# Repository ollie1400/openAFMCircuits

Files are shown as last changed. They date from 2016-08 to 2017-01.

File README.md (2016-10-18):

# openAFMCircuits

This is the repo for the circuit schematics and layouts for the openAFM board.  Each board is developed on a separate branch.  Current convention is that when the boards are complete and have been manufactured, they are merged with the main branch.  i.e. the main branch should always reflect the current state of the physical boards.

Each board is in a separate subfolder.  Some folders contain text files with "simulation" or "falstadsimulation" or something similar in the name.  These are schematics for a simulation (typically of some part of the circuit).  They can be viewed by going to http://www.falstad.com/circuit/circuitjs.html and importing the text via `File -> Import From Text`.

There are 4 boards that control the openAFM hardware.  These are

1. Main Board
2. Piezo Board
3. Voice Coil Board
4. Input Board

A brief descripion of each board is given below.  For more details look in the folder for each board.  Each board has a pair of 10-pin headers on either side.  These have a female connector on the top, and long lines that extend through the board and produte from the bottom.  These interboard headers allow the boards to stack on top of eachother, whilst sharing 20 common pins.

## Main Board

This board takes in 12V DC from the power supply.  It is responsible for regulating this down to 5V, and distributing power (12V, 5V and GND) to the other boards via the interboard headers.  It is responsible for generating a constant current for the laser diode in the DVD head, and routing signals from other boards (via the interboard headers) to the DVD head.  The DVD head connects directly to this board via a ribbon cable.  The board takes signals from the arduino (via the 10-pin female header) and routes them to the appropriate pins on the interboard headers to be shared with the other boards.

## Input Board

This board deals with the inputs from the 4 photodiode quadrants on the DVD head (labelled as A, B, C and D).  It routes these directly to an ADC, calculates differences and summs in hardware and routes these to another ADC.

## Piezo Board

This board has a 4 channel DAC which is used to control the signals to move each of the 4 piezo quadrants that control the stage movement.  It takes the 4 voltages from the DAC and amplifies them to give a larger range.

## Voice Coil Board

Has a DAC that, along with a pair of push-pull amplifiers, generates the required current to drive the voice coils in the DVD head (focus and tracking).

# I2C Addresses

Here are the I2C addresses of all ICs connected to the I2C bus.

**Part**  | AD5252BRUZ100 | AD5252BRUZ100 | AD5593RBRUZ | AD5696RARUZ | AD5696RARUZ
----------|---------------|---------------|-------------|-------------|------------
**Address (bin)** | 0101111 | 0101100 | 0010001 | 0001100 | 0001111
**Address (hex)** | 2F | 2C | 11 | C | F
**Address (dec)** | 47 | 44 | 17 | 12 | 15
**How?** | AD0 & AD1 to 5V | AD0 & AD1 grounded | A0 to 5V | A0 & A1 grounded | A0 & A1 to 5V
**Description** | Gain Dual digital pot | Gain Dual digital pot | Input ADC | Piezo DAC | Voice Coil DAC
**Board** | Input | Input | Input | Piezo | Voice Coil
**Board Label** | U2 | U6 | U3 | ? | ?

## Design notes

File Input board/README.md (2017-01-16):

# Input Board

This board deals with the photodiode signals from the DVD head.

# I2C Addresses

Here are the I2C addresses of the ICs on this board

**Part**  | AD5252BRUZ100 | AD5252BRUZ100 | AD5593RBRUZ
----------|---------------|---------------|-------------
**Address (bin)** | 0101111 | 0101100 | 0010001
**Address (hex)** | 2F | 2C | 11 
**Address (dec)** | 47 | 44 | 17
**How?** | AD0 & AD1 to 5V | AD0 & AD1 grounded | A0 to 5V
**Description** | Gain Dual digital pot | Gain Dual digital pot | ADC
**Board Label** | U2 | U6 | U3

# Layout Image

For ease of access here is the layout of the board (from the top)

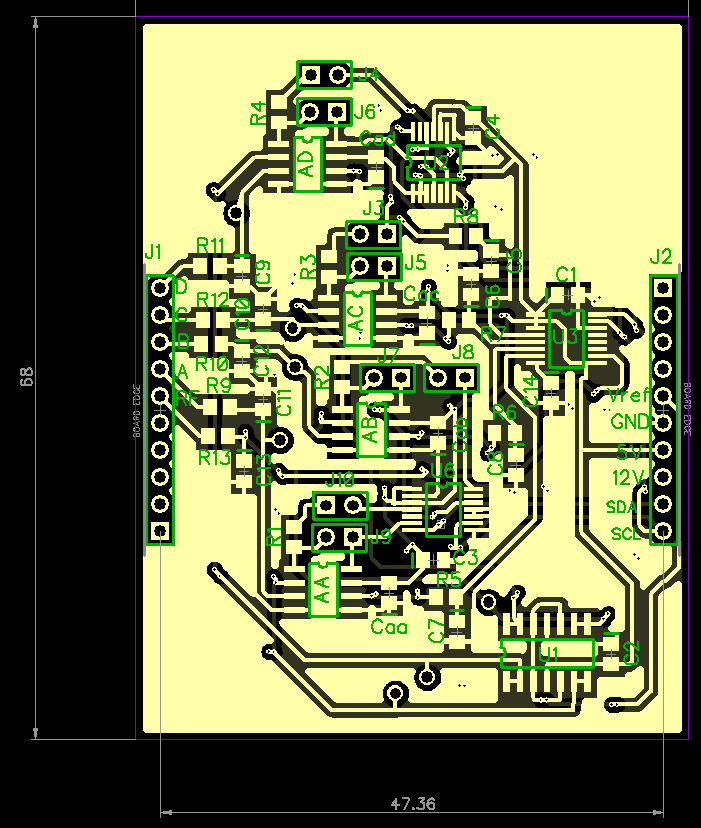
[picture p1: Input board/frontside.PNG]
Layout of front side of input board


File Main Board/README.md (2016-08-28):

# openAFMCircuits

This is the repo for the circuit schematics and layouts for the openAFM board.

There are 4 boards that control the openAFM hardware.  These are

1. Main Board
2. Piezo Board
3. Voice Coil Board
4. Input Board

In this repository, each board is on a different branch.

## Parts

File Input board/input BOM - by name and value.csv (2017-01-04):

RefDes | Value | Name | Pattern | Manufacturer | Quantity
AA, AB, AC, AD |  | AD623ARZ-R7 | SOIC-8/150mil | Analog Devices | 4
C1, C14 | 0.1u | CAP_0805 | CAP_0805 |  | 2
C2, C3, C4, C5, C6, C7, C8, C9, C10, C11, C12, C13, Caa, Cab, Cac, Cad | 3.2u | CAP_0805 | CAP_0805 |  | 16
J1, J2 |  | 1-644456-0 | HDR-1x10T/2.54/25x2 | TE Connectivity | 2
J3, J4, J5, J6, J7, J8, J9, J10 |  | 90131-0121 | HDR-2x1T/2.54x2.54/3x5 | Molex | 8
R1, R2, R3, R4 | 1k | RES_0805 | RES_0805 |  | 4
R5, R6, R7, R8, R9, R10, R11, R12, R13 | 5k | RES_0805 | RES_0805 |  | 9
U1 |  | LM324AD | SOIC-14/150mil | Motorola | 1
U2, U6 |  | AD5252BRUZ100 | TSSOP-14 | Analog Devices | 2
U3 |  | AD5593RBRUZ | TSSOP-16 | Analog Devices | 1
 |  |  |  |  | 49

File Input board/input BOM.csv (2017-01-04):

RefDes | Value | Name | Pattern | Manufacturer
AA |  | AD623ARZ-R7 | SOIC-8/150mil | Analog Devices
AB |  | AD623ARZ-R7 | SOIC-8/150mil | Analog Devices
AC |  | AD623ARZ-R7 | SOIC-8/150mil | Analog Devices
AD |  | AD623ARZ-R7 | SOIC-8/150mil | Analog Devices
C1 | 0.1u | CAP_0805 | CAP_0805
C2 | 3.2u | CAP_0805 | CAP_0805
C3 | 3.2u | CAP_0805 | CAP_0805
C4 | 3.2u | CAP_0805 | CAP_0805
C5 | 3.2u | CAP_0805 | CAP_0805
C6 | 3.2u | CAP_0805 | CAP_0805
C7 | 3.2u | CAP_0805 | CAP_0805
C8 | 3.2u | CAP_0805 | CAP_0805
C9 | 3.2u | CAP_0805 | CAP_0805
C10 | 3.2u | CAP_0805 | CAP_0805
C11 | 3.2u | CAP_0805 | CAP_0805
C12 | 3.2u | CAP_0805 | CAP_0805
C13 | 3.2u | CAP_0805 | CAP_0805
C14 | 0.1u | CAP_0805 | CAP_0805
Caa | 3.2u | CAP_0805 | CAP_0805
Cab | 3.2u | CAP_0805 | CAP_0805
Cac | 3.2u | CAP_0805 | CAP_0805
Cad | 3.2u | CAP_0805 | CAP_0805
J1 |  | 1-644456-0 | HDR-1x10T/2.54/25x2 | TE Connectivity
J2 |  | 1-644456-0 | HDR-1x10T/2.54/25x2 | TE Connectivity
J3 |  | 90131-0121 | HDR-2x1T/2.54x2.54/3x5 | Molex
J4 |  | 90131-0121 | HDR-2x1T/2.54x2.54/3x5 | Molex
J5 |  | 90131-0121 | HDR-2x1T/2.54x2.54/3x5 | Molex
J6 |  | 90131-0121 | HDR-2x1T/2.54x2.54/3x5 | Molex
J7 |  | 90131-0121 | HDR-2x1T/2.54x2.54/3x5 | Molex
J8 |  | 90131-0121 | HDR-2x1T/2.54x2.54/3x5 | Molex
J9 |  | 90131-0121 | HDR-2x1T/2.54x2.54/3x5 | Molex
J10 |  | 90131-0121 | HDR-2x1T/2.54x2.54/3x5 | Molex
R1 | 1k | RES_0805 | RES_0805
R2 | 1k | RES_0805 | RES_0805
R3 | 1k | RES_0805 | RES_0805
R4 | 1k | RES_0805 | RES_0805
R5 | 5k | RES_0805 | RES_0805
R6 | 5k | RES_0805 | RES_0805
R7 | 5k | RES_0805 | RES_0805
R8 | 5k | RES_0805 | RES_0805
R9 | 5k | RES_0805 | RES_0805
R10 | 5k | RES_0805 | RES_0805
R11 | 5k | RES_0805 | RES_0805
R12 | 5k | RES_0805 | RES_0805
R13 | 5k | RES_0805 | RES_0805
U1 |  | LM324AD | SOIC-14/150mil | Motorola
U2 |  | AD5252BRUZ100 | TSSOP-14 | Analog Devices
U3 |  | AD5593RBRUZ | TSSOP-16 | Analog Devices
U6 |  | AD5252BRUZ100 | TSSOP-14 | Analog Devices

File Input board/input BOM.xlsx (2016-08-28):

Description | Example URL | Quantity | Place Labels | Comments
3.2uF surface mount capacitors 0805 | http://china.rs-online.com/web/p/ceramic-multilayer-capacitors/7236054/ | 15 | C1, C2, ADC1Cap, ADC2Cap, Cref, Csr, C3, C4, C5, C6, C7, C8, ADCap1, ADCap2, OpCap | Can be anything from 3 to 3.4 uF
10k surface mount resistors 0805 | http://china.rs-online.com/web/p/surface-mount-fixed-resistors/2230562/ | 3 | Rr1, R2, Rr2 | Can be anything from 9.8k to 10.2k
5k surface mount resistors 0805 | http://china.rs-online.com/web/p/surface-mount-fixed-resistors/6791569/ | 12 | R1,R3, R4, R5, R7, R6, R8, R9,R10,R11, R12, R13 | Can be anything from 4.8k to 5.2k
ADS1015IDGSR | http://china.rs-online.com/web/p/general-purpose-adcs/7094550/ | 2 | ADS1015-1, ADS1015-2
AD623ARZ-R7 |  | 2 | AD623-1, AD623-2
30k surface mount resistors 0805 | http://china.rs-online.com/web/p/surface-mount-fixed-resistors/6791263/ | 2 | Rsr1, Rsr2 | Can be anything from 20k to 50k
10 pin female header | http://china.rs-online.com/web/p/pcb-sockets/7655745/ | 2 | J1, J2
2 pin male header | http://china.rs-online.com//web/p/pcb-headers/2518086/ (http://china.rs-online.com/web/p/pcb-headers/2518086/) | 2 | J3, J4
dual opamp, TL072CD | http://china.rs-online.com/web/p/operational-amplifiers/0857907/ | 1 | U1

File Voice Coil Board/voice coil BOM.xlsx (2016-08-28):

Description | Example URL | Label | Quantity
3.2uF surface mount capacitors 0805 | http://china.rs-online.com/web/p/ceramic-multilayer-capacitors/6911161/ | C1, C2, C3, C4, C11 | 4
10k surface mount resistors 0805 | http://china.rs-online.com/web/p/surface-mount-fixed-resistors/2230562/ | R6, R11, R12 | 3
5k surface mount resistors 0805 | http://china.rs-online.com/web/p/surface-mount-fixed-resistors/6791569/ | R1, R2, R3, R4, R7, R8, R9, R10 | 8
LM324D opamps | http://china.rs-online.com/web/p/operational-amplifiers/0858405/ | U9, U10 | 2
FMMT449 (NPN transistors) | http://china.rs-online.com/web/p/bipolar-transistors/6697681/ | U3, U4, U7, U8 | 4
FSB749 (PNP transistors) | http://china.rs-online.com/web/p/bipolar-transistors/8076033/?searchTerm=FSB749 | U1, U2, U5, U6 | 4
DAC (AD5338RBRUZ) | http://china.rs-online.com/web/p/general-purpose-dacs/8209173/?searchTerm=AD5338RBRUZ | DAC1 | 1
1k surface mount resistors 0805 | http://china.rs-online.com/web/p/surface-mount-fixed-resistors/2230427/ | R5 | 1
30k surface mount resistors 0805 | http://china.rs-online.com/web/p/surface-mount-fixed-resistors/6791263/ | R13, R14 | 2
10 pin female header | http://china.rs-online.com/web/p/pcb-sockets/7655745/ | J1, J2 | 2

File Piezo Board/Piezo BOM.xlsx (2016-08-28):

Description | Quantity | URL | Comments | Positions on board
3.2uF surface mount capacitors 0805 | 6 | http://china.rs-online.com/web/p/ceramic-multilayer-capacitors/6911161/ | Can vary from 3-3.5 uF | DaC, Cref, Ca, Cd, Cc, Cb
10k surface mount resistors 0805 | 3 | http://china.rs-online.com/web/p/surface-mount-fixed-resistors/2230562/ | Can vary from 10 to 50kOhm | Rdv1, Rdv2,Rdr
1uF surface mount capacitors 0805 | 1 | http://china.rs-online.com/web/p/ceramic-multilayer-capacitors/4515770/ | Must be 1uF | Cf
5k surface mount resistors 0805 | 8 | http://china.rs-online.com/web/p/surface-mount-fixed-resistors/6791569/ | Can vary from 4.8k to 5.2k | Ra1, Rb1, Rc1, Rd1, Rfa, Rfd, Rfc, Rfb
DAC (AD5696RARUZ) | 1 | http://china.rs-online.com/web/p/general-purpose-dacs/8065471/ |  | DAC1
LTC3260 | 1 | http://china.rs-online.com/web/p/charge-pumps/8516768/ | mounted so that pin 1 is next to the dot | <Unlabelled>
100k surface mount resistors 0805 | 2 | http://china.rs-online.com/web/p/surface-mount-fixed-resistors/2230691/ | Can vary from 90k to 110k | RAGm, RAGp
800k surface mount resistors 0805 | 2 | http://china.rs-online.com/web/p/surface-mount-fixed-resistors/7087004/ | can vary from 780k to 820k | RLAm, RLAp
200k surface mount resistor 0805 | 1 | http://china.rs-online.com/web/p/surface-mount-fixed-resistors/6791064/ | has to be 200k | R14
30k surface mount resistors 0805 | 4 | http://china.rs-online.com/web/p/surface-mount-fixed-resistors/6791263/ | can vary from 28k to 32k | Ra2, Rb2, Rc2, Rd2
10uF surface mount capacitors 0805 | 5 | http://china.rs-online.com/web/p/ceramic-multilayer-capacitors/6911161/ | Should be as close as possible | LmC, LpC, ViC, VoC, OC
10nF surface mount capacitors 0805 | 2 | http://china.rs-online.com/web/p/ceramic-multilayer-capacitors/2644371/ | Should be as close as possible | BmC, BpC
5 pin male header | 1 | http://china.rs-online.com/web/p/pcb-headers/2518121/?searchTerm=W81105T3825RC |  | Piezos
LM324AD | 1 | http://china.rs-online.com/web/p/operational-amplifiers/5171876/ |  | LM324

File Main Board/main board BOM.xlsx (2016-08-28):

Description | Example URL | Quantity | Label on PCB
20 Ohm surface mount resistor 0805 | http://china.rs-online.com/web/p/surface-mount-fixed-resistors/7217615/ | 1 | R7
1k surface mount resistors 0805 | http://china.rs-online.com/web/p/surface-mount-fixed-resistors/2230427/ | 1 | R1
4k7 surface mounts resistor 0805 | http://china.rs-online.com/web/p/surface-mount-fixed-resistors/2230528/ | 2 | R2, R3
10uF capacitor | http://china.rs-online.com/web/p/aluminium-capacitors/0117035/ | 3 | U4, C5, U8
10 pin female header | http://china.rs-online.com/web/p/pcb-sockets/7655745/ | 3 | J1, J5, Header for Arduino
2 pin male header | http://china.rs-online.com//web/p/pcb-headers/2518086/ (http://china.rs-online.com/web/p/pcb-headers/2518086/) | 2 | J6, J7,J3
220uF capacitors | http://china.rs-online.com/web/p/aluminium-capacitors/3150726/ | 2 | C16, C23
500k surface mount resistors 0805 | http://china.rs-online.com/web/p/surface-mount-fixed-resistors/6791437/ | 1 | R8
2A 100ohm ferrite bead | http://china.rs-online.com/web/p/ferrite-beads/6694159/?searchTerm=742792312 | 2 | U3, U34
L7809CV voltage regulator IC (TO-220V) | http://china.rs-online.com//web/p/linear-voltage-regulators/7140666/ (http://china.rs-online.com/web/p/linear-voltage-regulators/7140666/) | 1 | U6
L7805CV voltage regulator IC (TO-220V) | http://china.rs-online.com/web/p/linear-voltage-regulators/2988514/ | 1 | U7
LM4040 (SOT23) | http://china.rs-online.com/web/p/voltage-references/5457675/ | 1 | U9
24 pin 0.5mm pitch connector | http://uk.rs-online.com/web/p/fpc-connectors/8882721/ | 1 | U15
TVS SMB diode | http://china.rs-online.com//web/p/tvs-diodes/6287691/ (http://china.rs-online.com/web/p/tvs-diodes/6287691/) | 1 | U21
SPswitch on-off-on | http://china.rs-online.com/web/p/toggle-switches/1900557/ | 1 | U32
LM317TG single linear voltage regulator | http://china.rs-online.com/web/p/linear-voltage-regulators/5166240/ | 1 | U33
1uF SMT capacitors | http://china.rs-online.com/web/p/ceramic-multilayer-capacitors/4515770/ | 4 | C1, C3, C4, C17
100nF SMT capacitors | http://china.rs-online.com/web/p/ceramic-multilayer-capacitors/2644416/ | 2 | C2,C8
3 pin male header | http://china.rs-online.com/web/p/pcb-headers/2518092/ | 2 | J2, J4

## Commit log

2016-08-15 input board schematic
2016-08-15 Main board first schematic (NOT COMPLETE)
2016-08-15 Piezo board
2016-08-15 laying out the input board
2016-08-15 input board layout done + gitignore
2016-08-15 uploaded Tom's design for the previous board
2016-08-15 Latesst version of the piezo board
2016-08-15 Voice coil board (schematic and layout files)
2016-08-15 removed fixed gain resistors
2016-08-15 made board smaller. all resistors are 0805
2016-08-16 Changed labels on the layout to all be in the top silk. Expoted to Gerber. made list of parts.
    [BoardOutline.gbr, Bottom.gbr, BottomAssy.gbr, BottomDimension.gbr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]
2016-08-16 removed probably empty gerber files. Made new ones. had to move a label which was obscuring a pad.
    [BottomAssy.gbr, BottomDimension.gbr, BottomMask.gbr, BottomPaste.gbr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]
2016-08-16 removed input board, shouldn't be here
2016-08-16 Ignore temps. Removed the input board which is there...
2016-08-16 removed piezo board and main board
2016-08-16 Assigned resistor values and changed a few to use same values as the other boards.
2016-08-16 Swapped arduino for a header, as Esener designed a separate board for the arduino. Rewired the board to give space for the capacitors etc.
2016-08-16 Made Gerber files Made BOM : NEED TO FIND STUFF ON RS
    [BoardOutline.gbr, Bottom.gbr, Top.gbr, TopSilk.gbr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]
2016-08-16 started making order form. Made board a bit smaller
2016-08-16 Improved capacitor arrangement neatness
2016-08-16 Removed a random unused via. Redone gerber files. Proper size on the order form. Ignore temps
    [Bottom.gbr, Top.gbr]
2016-08-16 Added link for ADS
    [input BOM.xlsx]
2016-08-16 removed input boards
2016-08-16 Schematic and PCB all updated
2016-08-16 BLANK voice coil parts list
    [voice coil BOM.xlsx]
2016-08-16 Moved connector to board edge. Added PCB design of oldd board
2016-08-16 Fixed some pathing issue. Made new gerber ffiles. Started making list of parts.
    [BoardOutline.gbr, Bottom.gbr, Top.gbr, TopSilk.gbr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]
2016-08-16 New gerber files. Added labels in the BOM
    [Bottom.gbr, Top.gbr, input BOM.xlsx]
2016-08-16 Labels for voice coil components
    [voice coil BOM.xlsx]
2016-08-16 Made top Mask and Paste layers in gerber
    [TopMask.gbr, TopPaste.gbr]
2016-08-16 bottom mask
    [BottomMask.gbr]
2016-08-16 Added missing things to the schematic and layed out again. Have re-layed out the main board as mainboard2.
2016-08-17 Checked design rules. Made gerber and drill
    [BoardOutline.gbr, Bottom.gbr, BottomDimension.gbr, BottomMask.gbr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]
2016-08-17 checked BOM and zipped everything up
    [Piezo BOM.xlsx]
2016-08-17 updated COM and zipped things
    [voice coil BOM.xlsx]
2016-08-17 Ran DRC and generated the Gerber files
    [BoardOutline.gbr, Bottom.gbr, BottomAssy.gbr, BottomDimension.gbr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]
2016-08-17 added copper pour. Design rules checked. Order form done. Gerber and drill exported.
    [BoardOutline.gbr, Bottom.gbr, BottomAssy.gbr, BottomDimension.gbr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]
2016-08-17 done something. Making BOM
    [main board BOM.xlsx]
2016-08-17 fixed some components in the input BOM
    [input BOM.xlsx]
2016-08-17 new gerber files. Complete BOM.
    [Bottom.gbr, BottomMask.gbr, Through.drl, Top.gbr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]
2016-08-17 Piezo BOM was missing some parts, wrong parts...
    [Piezo BOM.xlsx]
2016-08-17 added to BOM, is now complete
    [input BOM.xlsx]
2016-08-17 corrected BOM, zipped up
    [voice coil BOM.xlsx]
2016-08-17 Removed unused assays
    [BottomAssy.gbr, TopAssy.gbr]
2016-08-18 falstad simulation of the amplifier stage
2016-08-22 Due to delay in sourcing the 2 channel DAC(AD5338RBRUZ), we decided to replace it with the 4 channel DAC (AD5696RARUZ) for component assembly. Rewired the address bit pins (A0 and A1) to 5V (now 11) 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
2016-08-22 Address pins updated on voice coils pin layout. Some redundant wiring and vias eliminated
2016-08-23 Added jumper and resistor between VRef and +5V Altered BOM parts so that Cf and R14 (for LTC3260) match datasheet Remade Gerber bits Sent to Donny
    [Bottom.gbr, BottomMask.gbr, Piezo BOM.xlsx, Through.drl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]
2016-08-26 Accounted for address change (11 instead of 00) and minor wire realignment
2016-08-28 Moved everything into into a subfolder to help merging to main
    [BoardOutline.gbr, Bottom.gbr, BottomAssy.gbr, BottomDimension.gbr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]
2016-08-28 Moved everything into a subfolder
    [BoardOutline.gbr, Bottom.gbr, BottomDimension.gbr, BottomMask.gbr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]
2016-08-28 Moved into sub folder
    [BoardOutline.gbr, Bottom.gbr, BottomAssy.gbr, BottomDimension.gbr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]
2016-08-28 more info about boards
2016-09-01 added more to the board descriptions
2016-09-01 made input board specific
2016-09-29 Added MCP4651 dual pot. Can be used to act as the gain resistors of the AD623s, by connecting a jumper. Header pins to allow manual pot are still there (with filters removed)
2016-09-29 added convention of master branch being the current board iteration
2016-10-06 connected A0 of the adc to 5V giving address of 0010001 = 0x09
2016-10-14 added 1k current limiting resistors for the gain digital pots. This limits the gain of the ad623 to <100 Added low pass filters on input to AD623s and to ADCs.
2016-10-14 Added 100nF cap betwen Vref of ADC and ground as required. Laid out board
2016-10-14 Made gerber files, drills, and BOM from diptrace
    [BoardOutline.gbr, Bottom.gbr, BottomAssy.gbr, BottomDimension.gbr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]
2016-10-14 new schematic, layout, gerber and BOM using AD5252BRUZ100 instead of the MCP4651-104E/ST for the digital pot.
    [Bottom.gbr, BottomMask.gbr, Through.drl, Top.gbr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]
2016-10-14 removed assay. zipped up new designs
    [BottomAssy.gbr, TopAssy.gbr]
2016-10-14 cleaned up a design problem
    [BoardOutline.gbr, Bottom.gbr, BottomAssy.gbr, BottomMask.gbr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]
2016-10-18 Fixed bug in schematic, using wrong ports on digital pot. Layed out for fabspace. Made gerber files etc.
    [BoardOutline.gbr, Bottom.gbr, BottomAssy.gbr, BottomDimension.gbr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]
2016-10-18 added input board i2c addresses from commit 46eeeea2ca901c45796758df1826c2b9d44c78b1
2016-10-18 just separate via and pad holes
    [Pads.drl, Vias.drl]
2016-11-21 better BOM and given missing capacitor values.
    [input BOM - by name and value.csv, input BOM.csv]
2016-11-21 added missing component values.
    [input BOM - by name and value.csv, input BOM.csv]
2017-01-16 image of board
